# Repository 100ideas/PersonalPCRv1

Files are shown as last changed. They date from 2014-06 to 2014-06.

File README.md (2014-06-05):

PersonalPCRv1
=============

### PersonalPCRv1 is a 2-tube arduino shield PCR thermocycler. Resistive heating, forced-air ambient cooling, no heated lid.

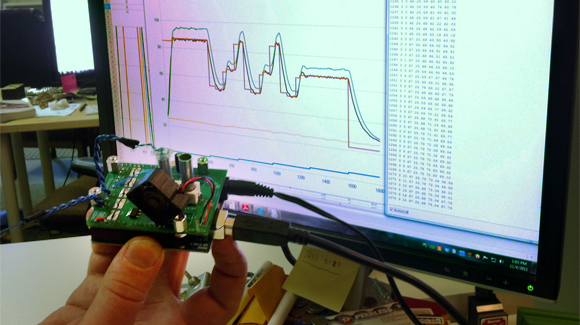
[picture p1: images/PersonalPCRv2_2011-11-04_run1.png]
PersonalPCRv2 2011-11-04 test run


PersonalPCRv1 was an open-source hardware collaboration between [Cofactor Bio LLC](https://web.archive.org/web/20120118133606/http://cofactorbio.com/personalpcr) and Templeman Automation LLC from 2011-2012. Cofactor wound down in 2012, Templeman wound down or severly curtailed operations in 2013. During operations, PersonalPCRv1 was available from Cofactor Bio for $149 + S/H. 

During 2012-13, the PersonalPCRv1 design evolved into an [8-tube strip resitive-heating / forced-air cooling thermocycler with heated lid](http://personalpcr.com) thanks to continued development at Templemen Automation. Later that year the company shut down and some of the developers tried to spin PersonalPCR off into a separate company. In May 2014 open-source harwdware reference files for PersonalPCRv2 were published at [personalpcr.com](http://personalpcr.com). Around this time, a new site was launched, MiniPCR.com. 

[MiniPCR.com](http://minipcr.com/), led by one of the original PersonalPCR developers from TA, manufactures and sells a thermocycler forked from the PersonalPCRv2 reference design. As of June 2014 they are unsure if they will continue the open-source tradition with their MiniPCR product. Assembled units start at $799.

Contents: hardware BOM, Arduino firmware, PCB design and fabrication files.

### More Images

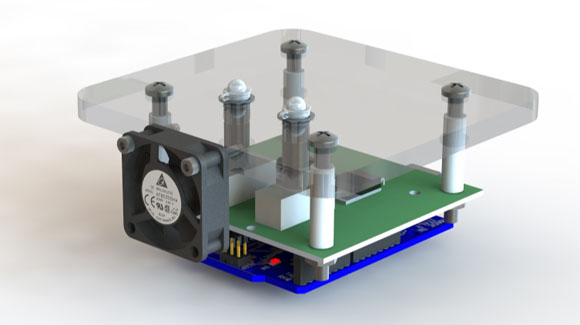
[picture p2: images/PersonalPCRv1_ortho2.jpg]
PersonalPCRv2 orthographic rendering


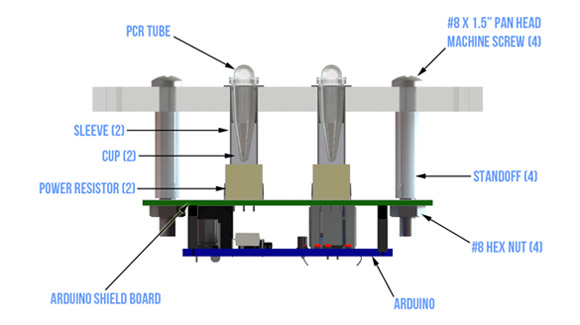
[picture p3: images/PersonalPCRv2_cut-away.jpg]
PersonalPCRv2 side-profile cutaway rendering


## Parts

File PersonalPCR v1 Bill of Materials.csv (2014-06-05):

Project: | PersonalPCR
Circuit Board Components
Part | Description | Value | Package | # | Manufact. | Man PN | Vendor | Vend PN
R1,R2,R3,R4,R5 | Resistor | 2000 Ohm | 1206 | 3 |  |  | Digikey | P2.00KFCT-ND
A0,A1,A2,A3,A4 | Thermistor | 2000 Ohm | Leaded | 3 |  |  | Digikey | 495-2144-ND
R6,R7,R8 | Resistor | 240 Ohm | 1206 | 2 |  |  | Digikey | 311-240ERCT-ND
R11,R14,R17 | Heater Resistor | 12 Ohm | TH | 1 | Yageo |  | Digikey | 12W-5-ND
C1 | Capacitor | 10 uF | 5x2mm TH | 1 | Panasonic | ECA-1CM101 | Digikey | P5138-ND
-- | Header | -- | 6 pin | 2 | 3M | 961106-6404-AR | Digikey | 3M9451-ND
-- | Header | -- | 8 pin | 2 | 3M | 961108-6404-AR | Digikey | 3M9452-ND
U1,U2,U3 | Transistor | --- | SOT-223 | 2 |  |  | Digikey | FZT600CT-ND
Fan and Power Supply
Part | Description | Value | Package | # | Manufact. | Man PN | Vendor | Vend PN
Extension Wire |  |  |  | 4 |  |  |  | misc
Heat Shrink |  |  |  | 4 |  |  |  | misc
Power Supply | 12V 2A Arduino Compatible |  |  | 1 |  |  |  | misc
FAN | FAN |  |  | 1 |  |  | Digikey | 259-1564-ND
Cap | Cap | 1uF | Leaded | 1 |  |  |  | misc
Tube Holder
Part | Description | Value | Package | # | Manufact. | Man PN | Vendor | Vend PN
Aluminum Tube | 9/32" OD Tube |  |  | 2 |  |  |  | misc
Aluminum Base | 1/4" OD Stock |  |  | 2 |  |  |  | misc
JB Weld | Epoxy |  |  | 1 |  |  |  | misc
Acylic Top | 1/4" Thick |  |  | 1 |  |  |  | misc
Standoffs |  |  |  | 4 |  |  | McMaster | 94639A664
Screws | 1.5” 4-40 |  |  | 4 |  |  | McMaster | 90276A119
Nuts | 4-40 |  |  | 4 |  |  | McMaster | 90480A005
NOTE: also check source BOM doc https://docs.google.com/spreadsheet/pub?key=0AvoYCobWBMh5dEljTXpmc19MSXRkVzA4d0dFUkpDNmc

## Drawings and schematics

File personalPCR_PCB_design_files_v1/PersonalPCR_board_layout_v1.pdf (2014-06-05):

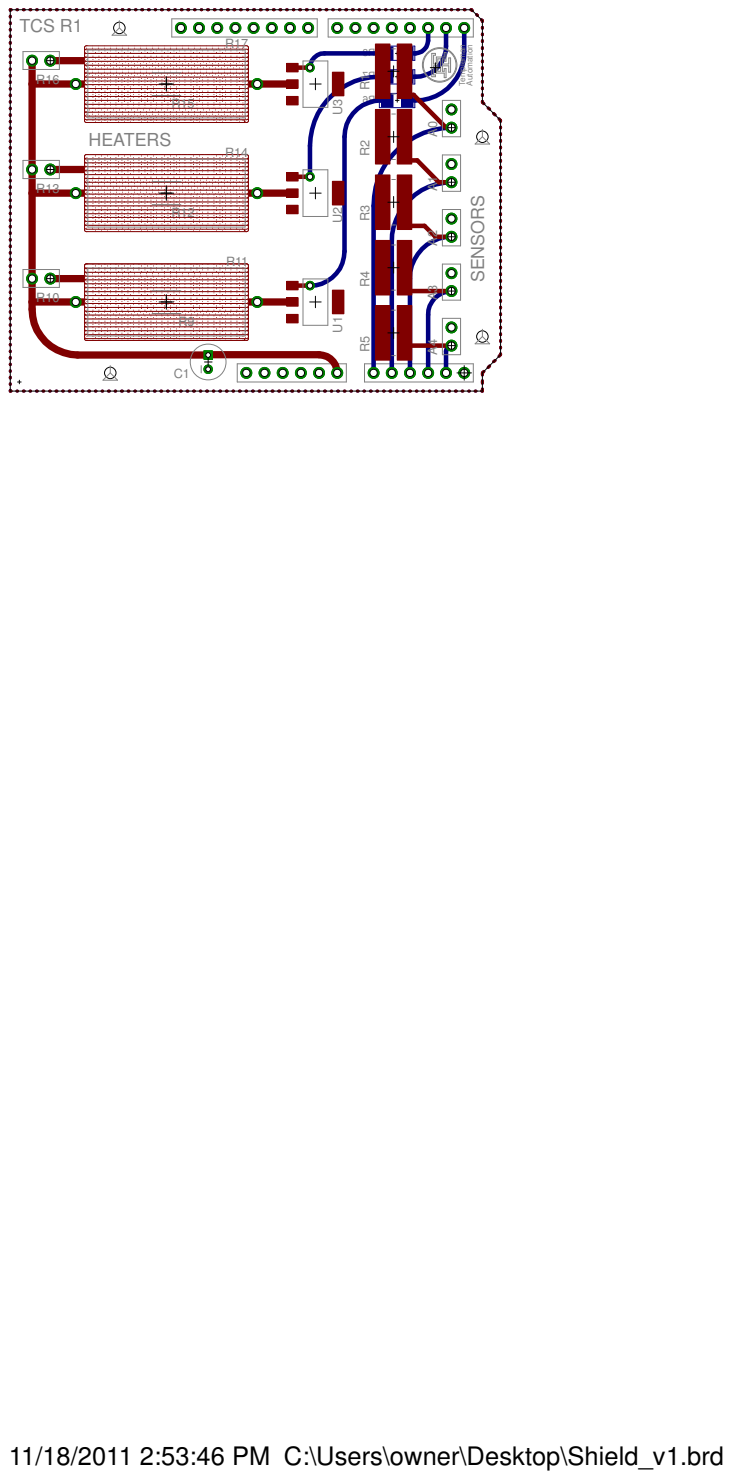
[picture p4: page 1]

11/18/2011 2:53:46 PM C:\Users\owner\Desktop\Shield_v1.brd

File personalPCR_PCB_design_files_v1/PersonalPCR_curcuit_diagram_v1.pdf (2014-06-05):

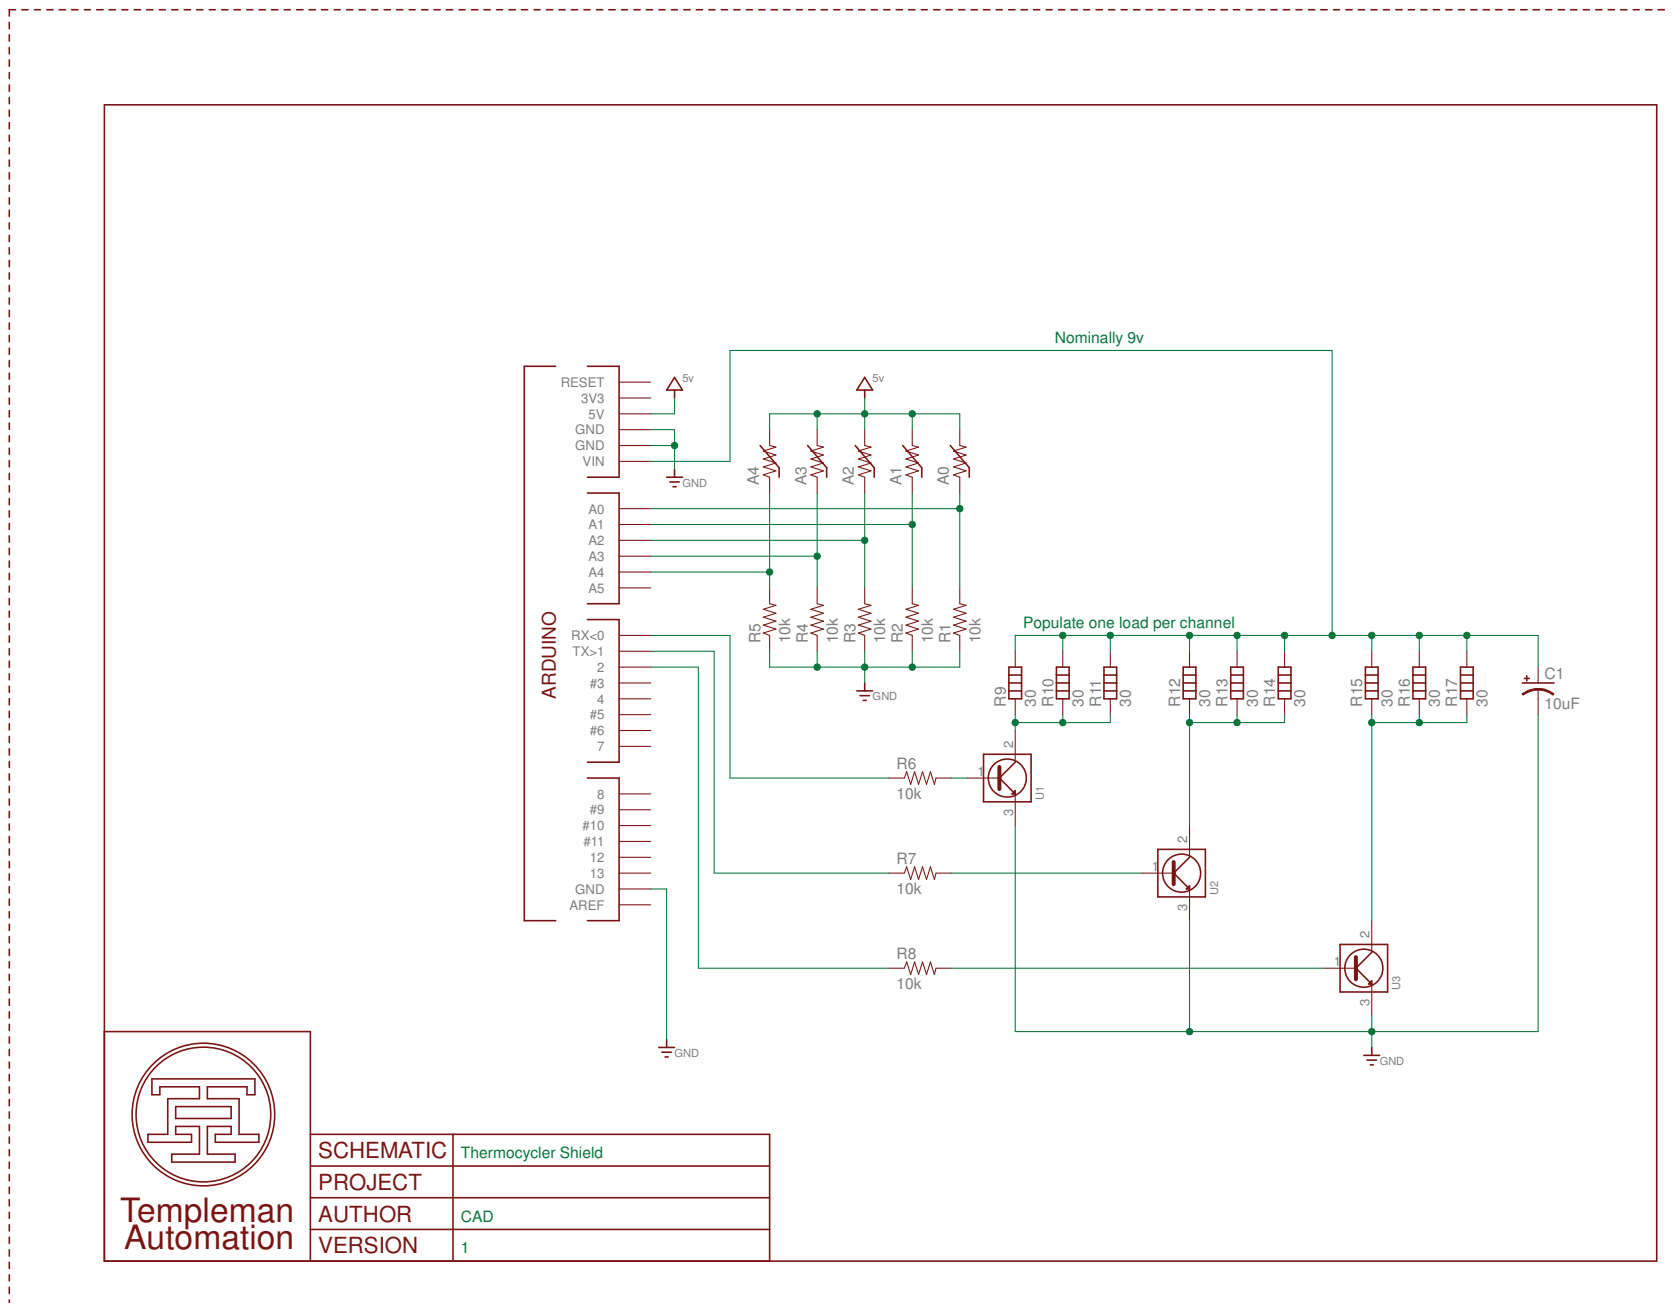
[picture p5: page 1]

Populate one load per channel

AUTHOR | CAD
VERSION | 1

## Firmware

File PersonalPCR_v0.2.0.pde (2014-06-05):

// PersonalPCR v0.2.0
// 11/16/2011
// templemanautomation.com
// coFactorbio.com

// PCR Temperatures in C
const float INITIALIZATION = 95;
const float DENATURATION = 95;
const float ANNEAL = 55;
const float EXTENSION = 72;
const float FINAL_ELONGATION = 72;
const float HOLD = 10;
const int NUMBER_OF_CYCLES = 30;

#include <math.h>
#define aref_voltage 5.0
#define TRUE 1
#define FALSE 0

// core functions
void settemperature(float settemp, int settime, int duty, int dolastdelay);
void rampup(float temp);
void rampdown(float temp);
void printData(float setTemp, int timer);
void readTemps();

const float TOLERANCE = 1;

const float DENATURATION_OFFSET = 4;
const float ANNEAL_OFFSET = 2;
const float EXTENSION_OFFSET = 3.5;

const int DENATURE_RAMP_OFFSET = 4 + DENATURATION_OFFSET;
const int ANNEAL_RAMP_OFFSET = 3 - ANNEAL_OFFSET;
const int EXTENSION_RAMP_OFFSET = 3 + EXTENSION_OFFSET;

int timer = 0;
unsigned long t = 0; 
int cycle = 0;

int heater = 3;
int fan = 2;

int sensorValue1 = 0;  
int sensorValue2 = 0; 
int sensorValue3 = 0; 

float temp1 = 0; 
float temp2 = 0;  
float temp3 = 0; 

float r1 = 0; 
float r2 = 0; 
float r3 = 0; 

const int analogInPin0 = A0; 
const int analogInPin1 = A1; 
const int analogInPin2 = A2; 


void setup() 
{
  Serial.begin(9600);
  pinMode(heater, OUTPUT);
  digitalWrite(heater, LOW);
  Serial.print("seconds");
  Serial.print(" "); 
  Serial.print("cycle_num");
  Serial.print(" "); 
  Serial.print("cycle_time");
  Serial.print(" "); 
  Serial.print("target_temp"); 
  Serial.print(" "); 
  Serial.print("probe_1_temp"); 
  Serial.print(" "); 
  Serial.print("probe_2_temp"); 
  Serial.print(" "); 
  Serial.print("control_temp");
  Serial.println(" "); 
 
}

void loop() 
{
  rampup(INITIALIZATION - DENATURE_RAMP_OFFSET);
  settemperature(INITIALIZATION - DENATURATION_OFFSET, 30, 50, TRUE); 
  for (int i = 0; i < NUMBER_OF_CYCLES ;i++)
  {
    cycle++;
    rampup(DENATURATION - DENATURE_RAMP_OFFSET);
    settemperature(DENATURATION - DENATURATION_OFFSET, 30, 50, TRUE);
    rampdown(ANNEAL + ANNEAL_RAMP_OFFSET);
    settemperature(ANNEAL - ANNEAL_OFFSET, 60, 30, TRUE);
    rampup(EXTENSION - EXTENSION_RAMP_OFFSET);
    settemperature(EXTENSION - EXTENSION_OFFSET, 60, 40, TRUE);
  }
  cycle++;
  settemperature(FINAL_ELONGATION - EXTENSION_OFFSET, 300, 50, TRUE);
  while (1)
  {
    rampdown(HOLD);
    settemperature(HOLD, 20, 50, TRUE);
  } 
}

void settemperature(float settemp, int settime, int duty, int dolastdelay)
{
  int i = 0;
  int timer = 0;
  int time2 = 0;
  time2 = settime * 10;
  int fanDuty = (100 - duty)/10;
  
  while (timer < time2)
  {
    readTemps();
    //display to serial monitor
    i++;
    t++;
    if (i == 10)
    {
      i=0;
      printData(settemp, timer);
    }
    
    if ( temp3 >= settemp)
    {
      digitalWrite(fan, HIGH);
    }
    if(temp3 < settemp + TOLERANCE){
      digitalWrite(heater, HIGH);
      delay(duty);
      digitalWrite(heater, LOW);
    }
    else {
      delay(duty);
    }
    
    if ((temp3 < (settemp + TOLERANCE)) && (temp3 > (settemp - TOLERANCE)))
    {
      timer = timer + 1;  
    }  
    if (dolastdelay)
    {
      delay(98 - duty - 20);
      digitalWrite(fan, LOW);
      delay(20);
    }      
  }
}

void readTemps() 
{ 
  //read all three sensors
  sensorValue1 = analogRead(analogInPin0);
  delay(1);
  sensorValue2 = analogRead(analogInPin1);
  delay(1);
  sensorValue3 = analogRead(analogInPin2);
  
  //convert all thermistors from "counts" voltage to C
  r1 = 2000.0*(1024.0/sensorValue1) - 2000.0;
  temp1 = 3560.0/log(r1/0.0130444106) - 273.15;
  r2 = 2000.0*(1024.0/sensorValue2) - 2000.0;
  temp2 = 3560.0/log(r2/0.0130444106) - 273.15;
  r3 = 2000.0*(1024.0/sensorValue3) - 2000.0;
  temp3 = 3560.0/log(r3/0.0130444106) - 273.15;
}

void printData(float setTemp, int timer)
{
    Serial.print(t / 10);
    Serial.print(" "); 
    Serial.print(cycle);
    Serial.print(" "); 
    Serial.print(timer / 10);
    Serial.print(" "); 
    Serial.print(setTemp);
    Serial.print(" "); 
    Serial.print(temp1); 
    Serial.print(" "); 
    Serial.print(temp2); 
    Serial.print(" "); 
    Serial.print(temp3);
    Serial.println(" "); 
}

void rampup(float temp)
{
   digitalWrite(heater, HIGH);
   int i = 0;
   readTemps();
   while(temp3 < temp) {
     readTemps();
    //display to serial monitor
    i++;
    t++;
    if (i == 10)
    {
      i=0;
      printData(temp, timer);
    }
    delay(100);     
   }
   digitalWrite(heater, LOW);
}

void rampdown(float temp)
{
   digitalWrite(fan, HIGH);
   int i = 0;
   readTemps();
   while(temp3 > temp) {
     readTemps();
    //display to serial monitor
    i++;
    t++;
    if (i == 10)
    {
      i=0;
      printData(temp, timer);
    }
    delay(100);     
   }
   digitalWrite(fan, LOW);
}
